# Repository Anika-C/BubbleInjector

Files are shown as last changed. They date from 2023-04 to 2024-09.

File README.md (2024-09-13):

# Bubble Injector

The Bubble Injector is a DIY scientific instrument designed to measure the fracture toughness (K<sub>Ic</sub>) of cohesive sediments using a bubble injection method. The system induces fracture in sediment samples by incrementally injecting air through a needle. The rising air pressure is monitored until it drops abruptly, indicating bubble formation. Fracture toughness is then calculated from the peak pressure at which fracture occurred. The system allows for measuring a depth profile with small-scale resolution and has produced measurements that compare well to past data.

This GitHub repository is meant to accompany the article: 
  Cho, Anika S., Dorgan, Kelly M., Lockridge, Grant. “Small-scale measurement of fracture toughness of muddy marine sediments via bubble injection.” Limnology and       Oceanography: Methods, vol. 22, no. 8, 18 May 2024, pp. 527–535,
  https://doi.org/10.1002/lom3.10625

## Hardware
  + Syringe Pump:
    + NEMA Stepper Motor
    + 3mL Syringe
    + 80/20 Linear Motion Bearing/Frame
    + Custom aluminum parts (CAD files available)
  + Electronics:
    + Arduino Zero + SD Card Shield
    + TinyG CNC Controller (v8)
    + 4-20mA Pressure Sensor (0-15 PSI)
    
Assembly details, full parts list, and cost estimate available in repo.

G-code & Setup Reference: https://github.com/synthetos/TinyG/wiki/Homing-and-Limits-Description-and-Operation

TinyG CNC Stepper Motor Controller configuration details: **TinyG_Config_Settings.txt**

## Code
**Bubble_Injection_Aug2022.ino**: Initiates automatic air injection procedures based on serial input, logs pressure sensor data to an SD card

**processBubble.m**: Plots pressure data, identifies critical peak pressure, and calculates (K<sub>Ic</sub>)

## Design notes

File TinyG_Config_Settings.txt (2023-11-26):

Adjust TinyG settings through the Arduino IDE
Serial input:
"$z" to display all settings for z axis 
"$3" to display all settings for m3 (motor 3, z axis)

Individually view and/or change settings:
Ex: "$3sa = ?" to view current ztm (z travel maximum) setting
Ex: "$3sa = 0.9" to change m3 step angle to 0.9 degrees

Zaxis Settings - 1/4-20 lead screw, 3mL syringe
[zam] z axis mode                 1 [standard]
[zvm] z velocity maximum        800 mm/min
[zfr] z feedrate maximum        800 mm/min
[ztn] z travel minimum         -160.000 mm
[ztm] z travel maximum           75.000 mm
[zjm] z jerk maximum             20 mm/min^3 * 1 million
[zjh] z jerk homing              40 mm/min^3 * 1 million
[zjd] z junction deviation        0.0500 mm 
[zsn] z switch min                0 [0=off,1=homing,2=limit,3=limit+homing]
[zsx] z switch max                3 [0=off,1=homing,2=limit,3=limit+homing]
[zsv] z search velocity          35 mm/min
[zlv] z latch velocity           15 mm/min
[zlb] z latch backoff             0.500 mm
[zzb] z zero backoff              3.300 mm

[3ma] m3 map to axis              2 [0=X,1=Y,2=Z...]
[3sa] m3 step angle               0.900 deg
[3tr] m3 travel per revolution    0.07463 mL		// 1/4-20 lead screw = 1.27mm/rotation
			    	  			// (1.27mm/rev) * (1mL/17.0168mm for 3mL syringe) = 0.07463mL/rev
[3mi] m3 microsteps               8 [1,2,4,8]
[3po] m3 polarity                 0 [0=normal,1=reverse]
[3pm] m3 power management         2 [0=disabled,1=always on,2=in cycle,3=when moving]

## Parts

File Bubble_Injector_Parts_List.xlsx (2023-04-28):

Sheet: Syringe_Pump
Syringe Pump Build Supply List
Item | Size/Specs | Supplier | Supplier PN | Cost Per | Count Total | Total | Link | Notes
Raw Stock
Aluminum T-slot Extrusion | 1 x 1 x 12 inch | 8020 | 1010 | $7.23 | 1 | $7.23 | https://8020.net/1010.html | T-Slotted Framing (#1)
Aluminum Bar | 3 x 5 x 1 inch |  |  |  |  |  |  | Syringe Barrel Holder (#3)
Aluminum Rod | 2.5 dia x 1.5 inch long |  |  |  |  |  |  | 3mL Syringe Adapter (#4)
Aluminum Bar | 3 x 5 x 1 inch |  |  |  |  |  |  | Syringe Plunger Mount (#5)
Aluminum Bar | 3 x 2.5 x 1 inch |  |  |  |  |  |  | Syringe Depressor Clamp (#6)
Aluminum Bar | 3 x 3 x 1 inch |  |  |  |  |  |  | Syringe Bearing End (#10)
Aluminum Bar | 0.5 x 0.5 x 10 inch |  |  |  |  |  |  | Cross Support (#12)
Parts
Single Mount Unibearing | 10 Series Short | 8020 | 6730 | $50.91 | 1 | $50.91 | https://8020.net/6730.html | Linear Bearing 8020 (#2)
3mL Syringe | Luer Lock Connection | McMaster | 7510A651 | $7.62 | 1 | $7.62 | https://www.mcmaster.com/7510A651/ | Pack of 10
Limit Switches |  | Amazon |  | $5.98 | 1 | $5.98 | https://www.amazon.com/HiLetgo-KW12-3-Roller-Switch-Normally/dp/B07X142VGC | Pack of 100
Shaft Coupling 1/4 inch to 5mm | 1/4 inch to 5mm | Amazon |  | $10.69 | 1 | $10.69 | https://www.amazon.com/Xnrtop-Coupling-Diameter-Aluminum-Connector/dp/B07YFMF2Z6 | Pack of 2
Stepper Motor | NEMA 17 | Amazon |  | $13.95 | 1 | $13.95 | https://www.amazon.com/STEPPERONLINE-Stepper-Bipolar-Connector-compatible/dp/B00PNEQKC0
Ball Bearing | R4 | McMaster Carr | 57155K305 | $6.42 | 2 | $12.84 | https://www.mcmaster.com/57155K305/
Hardware
6-32 x Socket Head Screw | 1/2 inch long, Stainless | McMaster Carr | 92196A148 | $8.72 | 1 | $8.72 | https://www.mcmaster.com/92196A148/ | Pack of 100
4-40 Socket Head Screw | 3/8 inch long, Stainless | McMaster Carr | 92196A108 | $6.30 | 1 | $6.30 | https://www.mcmaster.com/92196A108/ | Pack of 100
10-32 Socket Head Screw | 3/4 inch long, Stainless | McMaster Carr | 92196A272 | $19.56 | 1 | $19.56 | https://www.mcmaster.com/92196A272/ | Pack of 100
10-32 Socket Head Screw | 1/2 inch long, Stainless | McMaster Carr | 92196A269 | $15.47 | 1 | $15.47 | https://www.mcmaster.com/92196A269/ | Pack of 100
10-32 T Nut | Stainless | McMaster Carr | 94581A128 | $14.32 | 1 | $14.32 | https://www.mcmaster.com/94581A128/ | Pack of 10
1/4-20 Socket Head Screw | 3/4 inch long, Stainless | McMaster Carr | 92196A540 | $23.83 | 1 | $23.83 | https://www.mcmaster.com/92196A540/ | Pack of 50
1/4-20 Socket Head Screw | 3 inch long, Stainless | McMaster Carr | 92196A553 | $15.31 | 1 | $15.31 | https://www.mcmaster.com/92196A553/ | Pack of 10
1/4-20 Threaded Rod | 1 ft long, Stainless | McMaster Carr | 98804A487 | $2.31 | 1 | $2.31 | https://www.mcmaster.com/98804A487/
1/4-20 Nut |  | McMaster Carr | 92673A113 | $3.55 | 1 | $3.55 | https://www.mcmaster.com/92673A113/ | Pack of 50
M3 x 0.35 Socket Head Screw | 16 mm long, Stainless | McMaster Carr | 90751A114 | $15.73 | 1 | $15.73 | https://www.mcmaster.com/90751A114/ | Pack of 100
 |  |  |  |  | TOTAL | $234.32

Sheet: Electonics_Controller
Electronics Control Box Supply List
Item | Size/Specs | Supplier | Supplier PN | Cost per | Count total | Total | Link | Notes
Boards/Sensors
Arduino Zero |  | Amazon | ABX00003 | $49.50 | 1 | $49.50 | https://www.amazon.com/Arduino-Zero-ABX00003/dp/B09CMCXVV4
SD Card Shield |  | Adafruit | 1141 | $13.95 | 1 | $13.95 | https://www.adafruit.com/product/1141
Screw Shield R3 |  | Adafruit | 196 | $14.95 | 1 | $14.95 | https://www.adafruit.com/product/196
TinyG Controller v8 |  | Adafruit | 1749 | $165.00 | 1 | $165.00 | https://www.adafruit.com/product/1749
Voltage Adapter | AC110 to 24VDC 4A | Amazon |  | $8.46 | 1 | $8.46 | https://www.amazon.com/Switch-Supply-Module-Isolated-Output/dp/B07GWCPTQB
Pressure Sensor | 4-20mA, 0-15psig | Omega | PX309-015GI | $331.43 | 1 | $331.43 | https://www.omega.com/en-us/pressure-measurement/pressure-transducers/px309/p/PX309-015GI
Components/Hardware
Screw Terminal | 5mm pitch, 2 pos | Mouser | 490-TB002-500-02BE | $0.65 | 1 | $0.65 | https://www.mouser.com/ProductDetail/CUI-Devices/TB002-500-02BE?qs=vLWxofP3U2x9716kcgva%2Fw%3D%3D
Terminal Block | 20A, 300VAC, 4 pos | McMaster Carr | 7527K44 | $2.54 | 1 | $2.54 | https://www.mcmaster.com/7527K44/
Fuse Holder | 6 x 32mm fuse | Mouser | 504-BK2-S-4202-1X-R | $1.95 | 1 | $1.95 | https://www.mouser.com/ProductDetail/Bussmann-Eaton/BK2-S-4202-1X-R?qs=DRkmTr78QASifKBhsRdWiQ%3D%3D
Din 5 pin bulkhead |  | Amazon |  | $6.99 | 1 | $6.99 | https://www.amazon.com/CESS-Female-Socket-Connector-Soldering/dp/B01GBT9RC0 | Pack of 4
USB Bulkhead |  | Amazon |  | $13.89 | 1 | $13.89 | https://www.amazon.com/Anmbest-Electrical-Waterproof-Connector-Industrial/dp/B07RPW5XGB/ | Pack of 2
AC Power Socket Male | 10A, 250V | Amazon |  | $7.99 | 1 | $7.99 | https://www.amazon.com/button-Adapter-Connector-Socket-MXRS/dp/B082ZFRV1B | Pack of 3
Circuit Components
Resistor | 390 ohm, 1/4 watt | Mouser | 708-RNMF14FAD390R | $0.01 | 1 | $0.01 | https://www.mouser.com/ProductDetail/SEI-Stackpole/RNMF14FAD390R
Tantalum Capacitor | 1 uF | Mouser | 581-TAP105M050CRW | $0.85 | 1 | $0.85 | https://www.mouser.com/ProductDetail/AVX/TAP105M050CRW/?qs=D60Q9NgkslkPfEe0TVgP8Q%3D%3D
Tantalum Capacitor | 0.1 uF | Mouser | 80-T356A104K35AT | $1.31 | 1 | $1.31 | https://www.mouser.com/ProductDetail/KEMET/T356A104K035AT
Zener Diode | 3.6v, 5.1watt | Amazon |  | $4.99 | 1 | $4.99 | https://www.amazon.com/1N4733A-1N4733-Silicon-Planar-DO-204AL/dp/B07WK46MK4?th=1 | Pack of 20
 |  |  |  |  | TOTAL | $624.46

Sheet: Assembly
Bubble Injector Assembly Supply List
Item | Size/Specs | Supplier | Supplier PN | Cost per | Count total | Total | Link | Notes
Air Injection System
14G Dispensing Needle | 2 inch long, Point Style 5 (Non-Coring), Luer Lock | Hamilton | 7746-15 | $133.00 | 1 | $133.00 | https://www.hamiltoncompany.com/laboratory-products/needles/7746-15 | Pack of 6
22G Dispensing Needle | 2 inch long, Point Style 5 (Non-Coring), Luer Lock | Hamilton | 7746-06 | $133.00 | 1 | $133.00 | https://www.hamiltoncompany.com/laboratory-products/needles/7746-06 | Pack of 6
1/4" Tubing | Clear, 5/32" ID | McMaster | 5648K69 | $0.65 | 2 | $1.30 | https://www.mcmaster.com/5648K69-5648K256/ | Per Foot
Stop Valve | Male x Female, Luer Lock | McMaster | 7033T24 | $2.66 | 1 | $2.66 | https://www.mcmaster.com/7033T24/
Threaded Tube Coupling | 10-32 x Male Adapter, Luer Lock | McMaster | 51525K428 | $6.72 | 1 | $6.72 | https://www.mcmaster.com/51525K428/ | Pack of 10
Female Tube Coupling | 5/32" Tube ID x Female Luer Lock | McMaster | 51525K214 | $5.09 | 1 | $5.09 | https://www.mcmaster.com/51525K214/ | Pack of 10
Male Tube Coupling | 5/32" Tube ID x Male Luer Lock | McMaster | 51525K124 | $6.26 | 1 | $6.26 | https://www.mcmaster.com/51525K124/ | Pack of 10
Assembly & Testing Materials
Multi-Axis Manual Micromanipulator | 3mm - 12.7mm Tool Clamp |  |  |  |  |  | https://www.wpi-europe.com/products/micromanipulators/manual-manipulators/m325.aspx | Used part unavailable, substitute part linked
10mm Steel Rod | 1-1/2 feet long | McMaster | 1272T41 | $26.92 | 1 | $26.92 | https://www.mcmaster.com/1272T41-1272T412/ | Micromanipulator mount
Aluminum Tubing | 1/4" OD, 0.02" Wall Thickness | McMaster | 89965K341 | $7.16 | 1 | $7.16 | https://www.mcmaster.com/89965K341/ | Per Foot
1/4" Acrylic Stock | 12 x 12 x 0.25 inch, Clear | McMaster | 8560K354 | $18.38 | 2 | $36.76 | https://www.mcmaster.com/8560K354/ | Platform
1/4" Aluminum Unthreaded Spacer | 1/4" Screw Size, 1-1/2 inch long | McMaster | 92510A771 | $4.25 | 4 | $17.00 | https://www.mcmaster.com/92510A771/ | Platform Spacers
1/4-20 Hex Head Screw | 2-1/2 inch long | McMaster | 92240A552 | $7.74 | 1 | $7.74 | https://www.mcmaster.com/92240A552/ | Pack of 25
6" Plastic Dish | 0.75 inch depth, Clear | Amazon |  | $9.39 | 1 | $9.39 | https://www.amazon.com/Plastic-Petri-Dish-Lid-Polypropylene/dp/B08X4VD3XY
4" (10cm) Acrylic Tube | 12 inch long, Clear | Amazon |  | $7.86 | 1 | $7.86 | https://www.amazon.com/FixtureDisplays-Acrylic-Diameter-15139-12-1PK-NF/dp/B086KT4F8N | Testing Core
 |  |  |  |  | TOTAL | $400.86

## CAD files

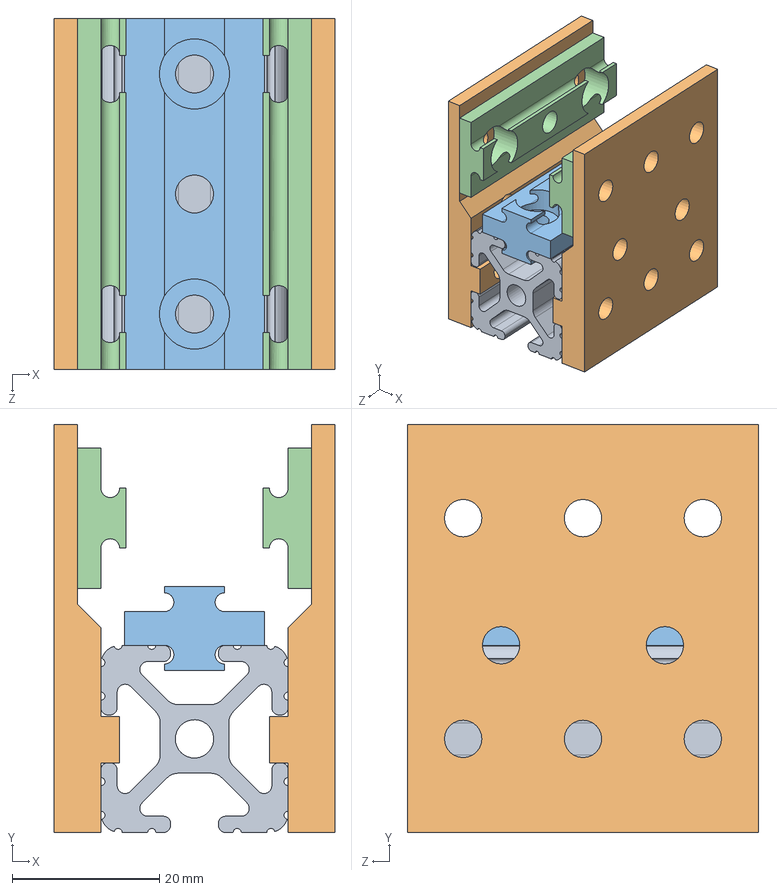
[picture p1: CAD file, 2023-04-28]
Syringe Pump CAD Model/LinearBearing_8020_pn6730.SLDASM
38.1 x 55.3 x 47.6 mm
T-Slotted Framing_1.875
BearingSide x 2
Pad_Bearing_Upper
Pad_Bearing x 2

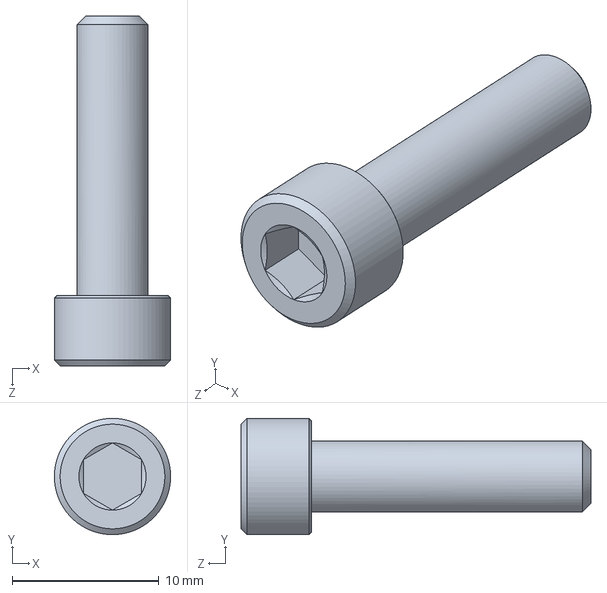
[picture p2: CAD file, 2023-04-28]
Syringe Pump CAD Model/Hardware/10-32_x0.75_ SocketHead.SLDPRT
7.94 x 7.94 x 23.9 mm

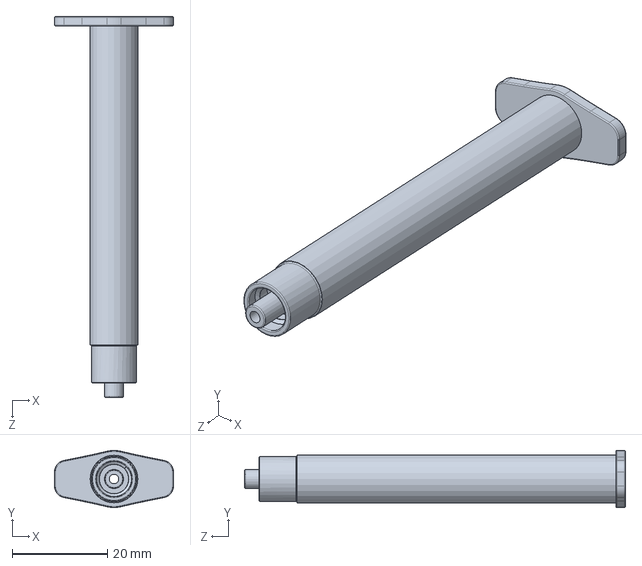
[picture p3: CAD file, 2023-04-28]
Syringe Pump CAD Model/Hardware/syringe 3ml part 01.SLDPRT
25.0 x 12.0 x 80.0 mm

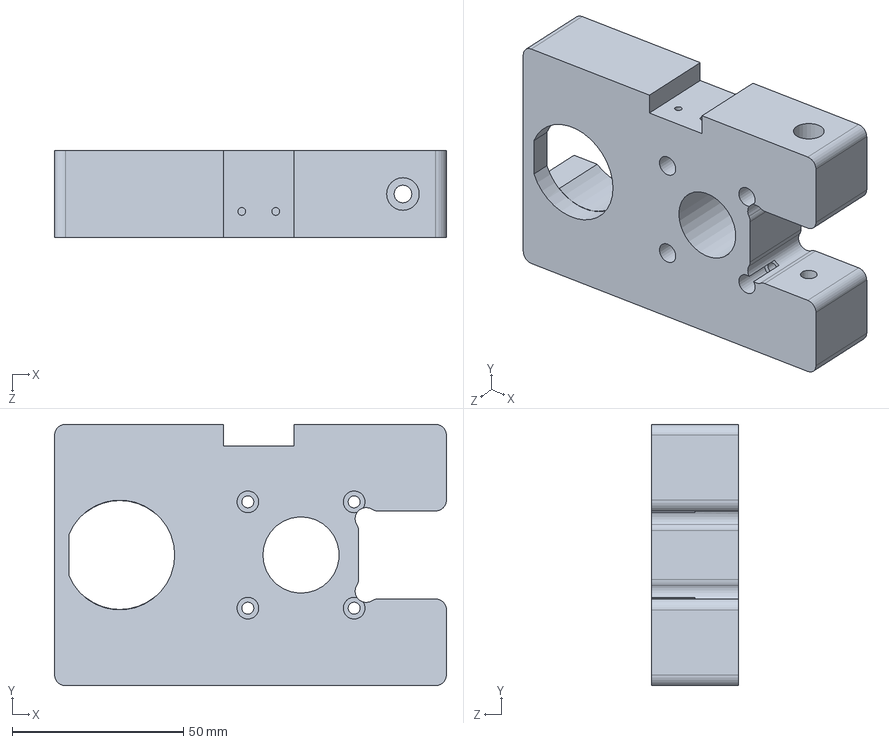
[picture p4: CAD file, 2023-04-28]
Syringe Pump CAD Model/Syringe_Plunger_Mount_v1.SLDPRT
114.3 x 76.2 x 25.4 mm

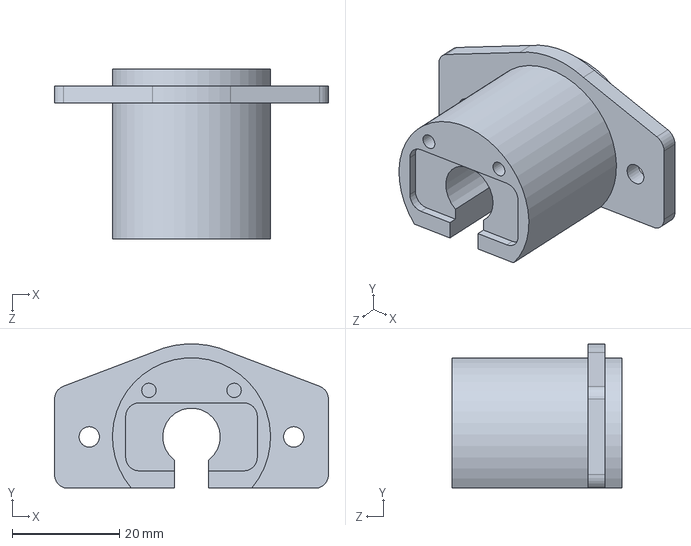
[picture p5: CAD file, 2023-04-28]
Syringe Pump CAD Model/3mL_Adapter_v1.SLDPRT
51.1 x 26.8 x 31.8 mm

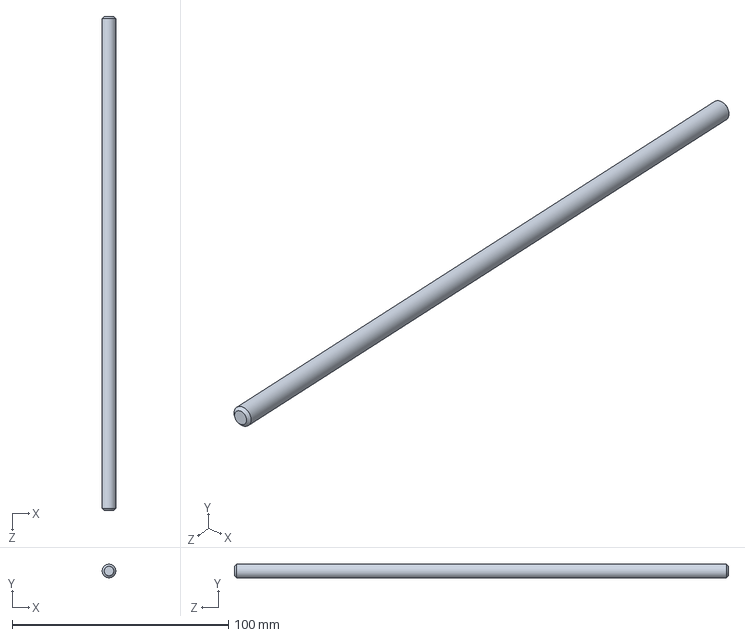
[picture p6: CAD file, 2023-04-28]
Syringe Pump CAD Model/Hardware/1_4-20_Threaded Rod_10in.SLDPRT
6.35 x 6.35 x 228.6 mm

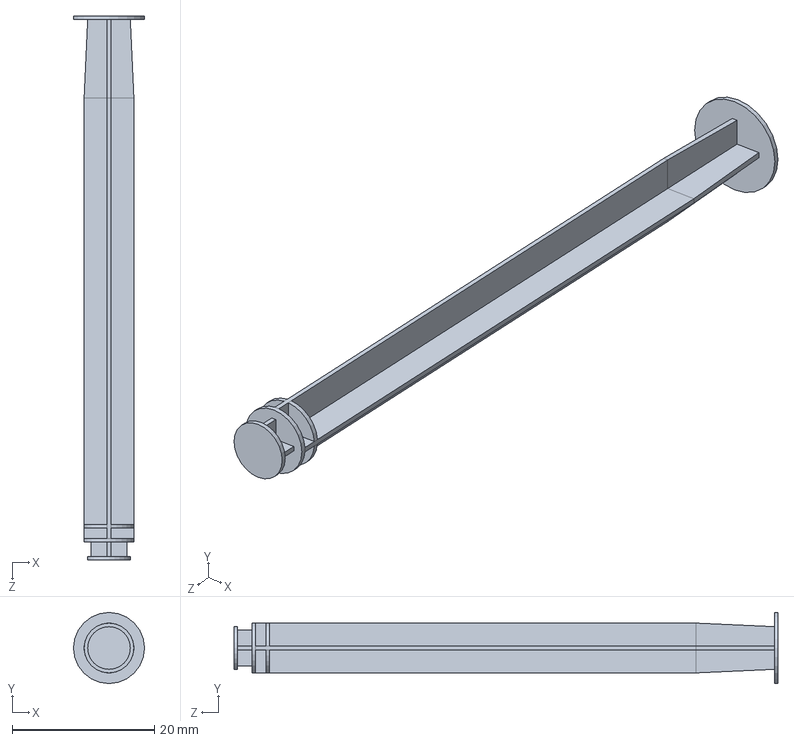
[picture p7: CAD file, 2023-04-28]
Syringe Pump CAD Model/Hardware/syringe 3ml part 02.SLDPRT
10.0 x 10.0 x 76.5 mm

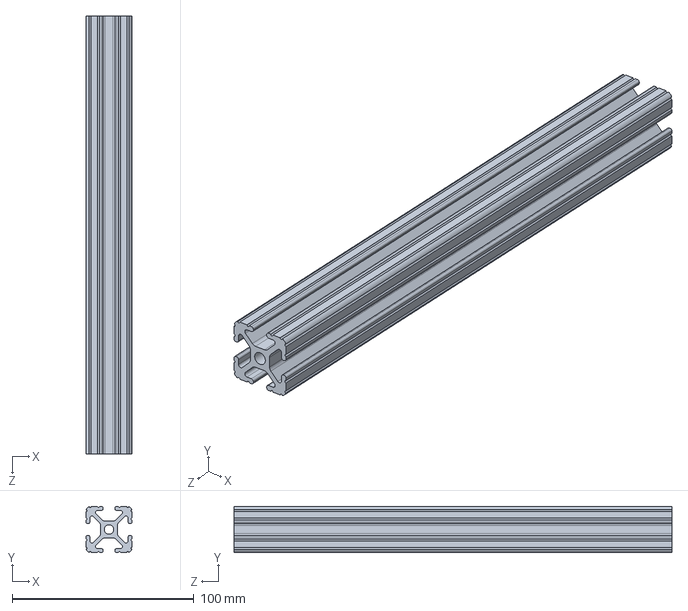
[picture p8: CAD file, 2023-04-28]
Syringe Pump CAD Model/T-Slotted Framing12.SLDPRT
25.4 x 25.4 x 241.3 mm

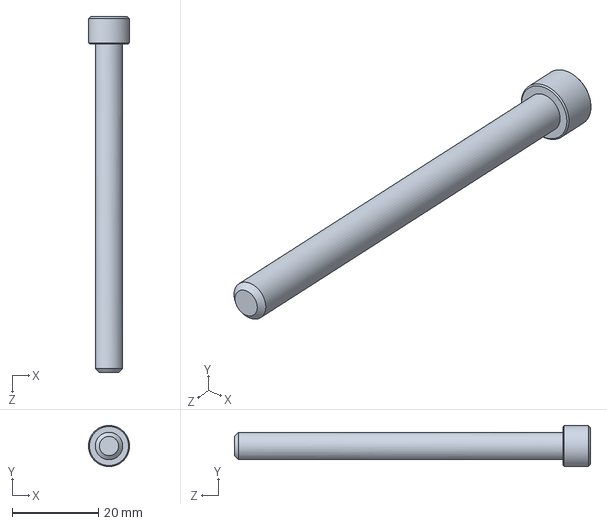
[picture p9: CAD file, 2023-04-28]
Syringe Pump CAD Model/Hardware/1_4-20_x3_ SocketHead.SLDPRT
9.53 x 9.52 x 82.5 mm

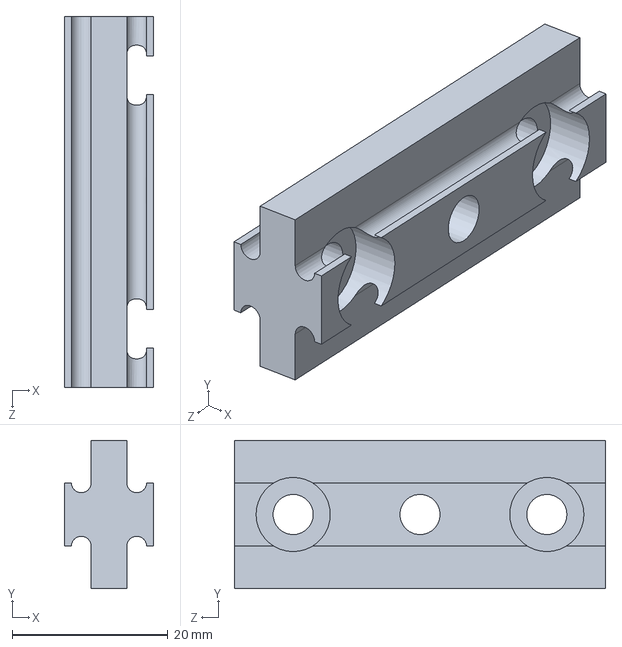
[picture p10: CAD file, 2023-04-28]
Syringe Pump CAD Model/Pad_Bearing_Upper.SLDPRT
11.4 x 19.1 x 47.6 mm

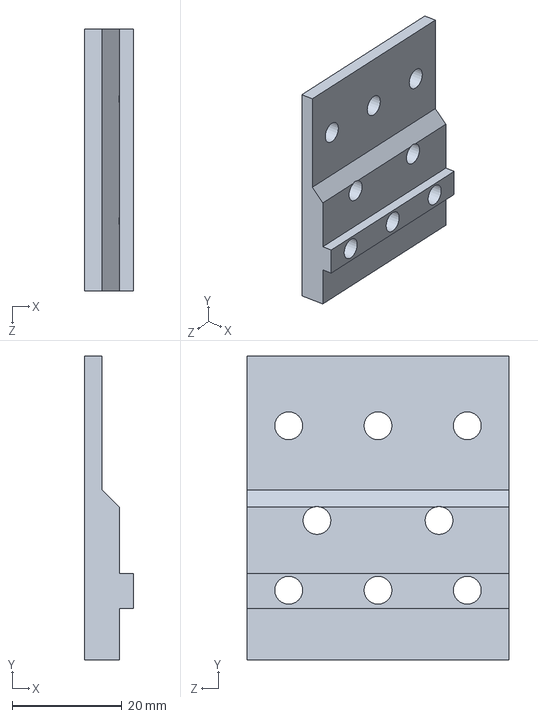
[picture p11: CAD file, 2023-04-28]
Syringe Pump CAD Model/BearingSide.SLDPRT
8.89 x 55.3 x 47.6 mm

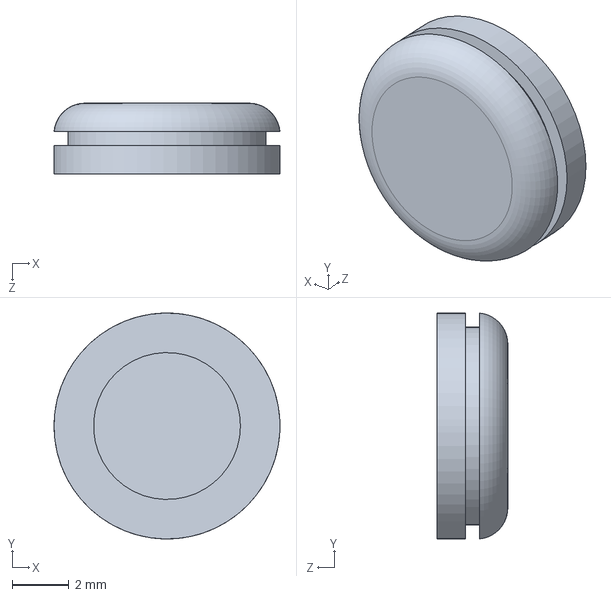
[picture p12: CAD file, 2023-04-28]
Syringe Pump CAD Model/Hardware/syringe 3ml part 03.SLDPRT
7.99 x 7.99 x 2.50 mm

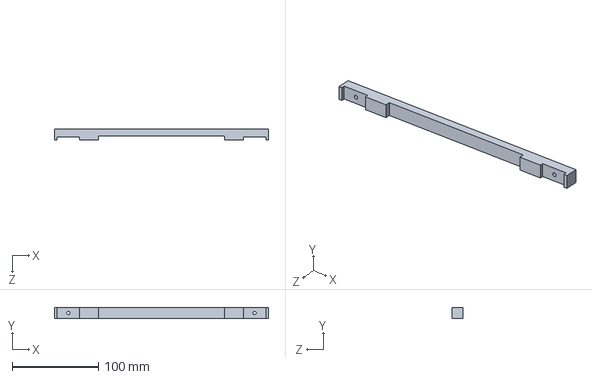
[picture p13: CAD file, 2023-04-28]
Syringe Pump CAD Model/CrossSupport_v1.SLDPRT
247.9 x 12.7 x 12.7 mm

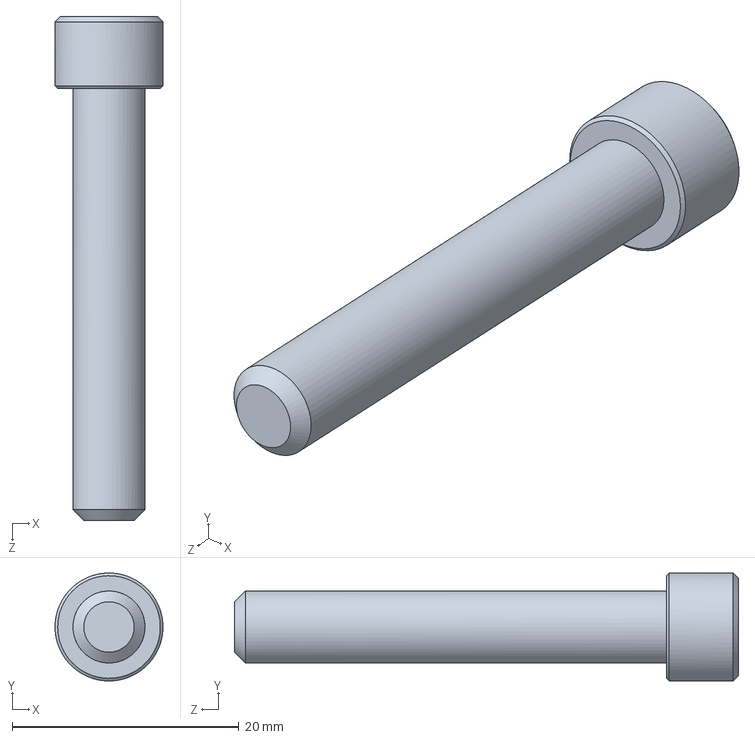
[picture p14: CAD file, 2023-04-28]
Syringe Pump CAD Model/Hardware/1_4-20_x1.5_ SocketHead.SLDPRT
9.53 x 9.52 x 44.5 mm

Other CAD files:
Syringe Pump CAD Model/Hardware/limit switch.SLDPRT
Syringe Pump CAD Model/Omega Pressure Transducer.SLDPRT
Syringe Pump CAD Model/Syringe_Depres_Clamp_V1.1.SLDPRT
Syringe Pump CAD Model/SyringeBarrelHolder_v1.SLDPRT
Syringe Pump CAD Model/Hardware/10-32_T_Nut.SLDPRT
Syringe Pump CAD Model/Hardware/10-32_x0.5_ SocketHead.SLDPRT
Syringe Pump CAD Model/Hardware/1_4-20_x0.75_ SocketHead.SLDPRT
Syringe Pump CAD Model/Hardware/4-40_x0.375_ SocketHead.SLDPRT
Syringe Pump CAD Model/Hardware/6_32_x0.5_SocketHead.SLDPRT
Syringe Pump CAD Model/Hardware/M3_16mm_SocketHead.SLDPRT
Syringe Pump CAD Model/Hardware/NEMA17_Stepper Motor.SLDPRT
Syringe Pump CAD Model/Hardware/R4_BallBearing.SLDPRT
Syringe Pump CAD Model/Hardware/Shaft Coupling 5mm to 1_4.SLDPRT
Syringe Pump CAD Model/Hardware/T_Nut_Assembly.SLDASM
Syringe Pump CAD Model/Hardware/T_Nut_Assembly_0.75.SLDASM
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

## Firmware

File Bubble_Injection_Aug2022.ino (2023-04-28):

/*
 * Anika Cho
 * Dorgan Lab, Summer 2022
 * Bubble Injection Procedure Code
 * Updated August 2022
 * 
 * Setup: 
 * Mud sample should be extruded into a pre-drilled test core with all bubble injection holes thoroughly taped closed
 * Check connections: USB power from computer to Arduino Zero, standard wall outlet to power supply/electronics box, stepper motor cable to "Z axis" port, pressure sensor & Z-limit switch to labelled USB ports
 * Place the test core in the tray and slide into the circular slot on the test platform
 * Upload this Bubble Injection program to the Arduino Zero
 * 
 * Bubble Injection Testing Procedure:
 * 1) Reset the syringe by entering the command "r" to the serial monitor/plotter
 * 2) Check the needle for clogs by flushing the needle with warm water and air using a hand-held syringe
 *    Use 14G non-coring needle for mud, 22G non-coring needle for jello
 * 3) Firmly screw the needle into the stop valve with the needle port oriented sideways, then use the micromanipulator to align the needle with an injection hole
 * 4) Use the micromanipulator to fully insert the needle into the sediment core through the tape
 * 4) Verify that the SD Card is in the SD Card Shield and hit the Reset button on the Arduino Zero to begin logging pressure data to a new file
 * 5) Input the chosen procedure command to the serial monitor/plotter to begin the air injection cycle
 *    ("j" for jello, "m" for mud)
 * 6) Monitor the live pressure plot generated by the serial plotter until a clear pressure drop is observed (bubble formation)
 *    Orange line = Pressure (PSI), Grey line = Analog Voltage Input
 * 7) Hit the Reset button on the TinyG board to stop air injection after bubble formation
 * 8) Remove the SD card to stop logging pressure data and save the file
 * 9) Fully retract the needle from the core and tape over the puncture hole to prevent water leakage
 */

//*********************************** INITIAL SETUP ***********************************************

#include <Wire.h>
#include <Adafruit_ADS1X15.h>
#include <SPI.h>
#include <SD.h>

// Number of milliseconds between grabbing and logging data. 1000 ms = once a second
#define LOG_INTERVAL  10    // ms between entries (reduce to take more/faster data)

// Number of milliseconds before writing the logged data permanently to disk
// Set to the LOG_INTERVAL to write each time (safest)
// Set to 10*LOG_INTERVAL to write all data every 10 datareads
// Could lose the last 10 datareads if power is lost, but consumes less power & is much faster!
#define SYNC_INTERVAL 100 // mills between calls to flush() - to write data to the card

uint32_t syncTime = 0;      // time of last sync()

#define ECHO_TO_SERIAL   1  // echo data to serial port
#define WAIT_TO_START    0  // Wait for serial input in setup()

// For the data logging shield, we use digital pin 10 for the SD cs line
const int chipSelect = 10;  //THIS NEEDS TO BE JUMPED FROM THE NORMAL PIN 10 ON THE SD CARD SHIELD

// Data logging file
File logfile;


//*********************************** TEST ARDUINO COMMS ***********************************************

int val = 0;
void error(char *str)
{
  SerialUSB.print("error: ");
  SerialUSB.println(str);
  while (1);
}

//*********************************** CAPTURE SERIAL DATA FROM TINYG ***********************************************

const byte numChars = 43;
char receivedChars[numChars];
char tempChars[numChars];        // temporary array for use when parsing

// variables to hold the parsed data
char messageFromPC[numChars] = {0};
int integerFromPC = 0;
float floatFromPC = 0.0;
float Zpos = 0.000;
float Apos = 0.000;
boolean newData = false;

//*********************************** PRESSURE SENSOR SETUP ***********************************************

const int pressureSensorIn = A1;  // analog input pin that the pressure sensor is attached to
int sensorValue = 0;              // value read from the pressure sensor
float PSI = 0;                    // value output to the PWM (analog out)
float sensorVolt = 0;             // voltage from the pressure sensor
  
Adafruit_ADS1015 ads;     /* Use this for the 12-bit version */


//*********************************** BUTTONS ***********************************************

const int buttonD8 = 8 ; // button with pin
int buttonStateD8 = 0 ;

const int buttonD5 = 5 ; // button with pin
int buttonStateD5 = 0 ;

const int buttonD6 = 6 ; // button with pin
int buttonStateD6 = 0 ;

const int buttonD7 = 7 ; // button with pin
int buttonStateD7 = 0 ;


//*********************************** SETUP SERIAL COMMS & SD CARD LOG FILE ***********************************************

void setup()
{
  SerialUSB.begin (115200);
  Serial1.begin (115200);
  Serial.begin (115200);

  pinMode(buttonD8, INPUT);
  pinMode(buttonD5, INPUT);
  pinMode(buttonD6, INPUT);
  pinMode(buttonD7, INPUT);

  delay (500); // setting TinyG position output

  Serial1.println("?");
  Serial1.println("{\"sr\":{\"posx\":t, \"posy\":t,\"posz\":t,\"posa\":t}}");
  Serial1.println("$qv=0");  // setting the Queue Report Verbosity to zero (disable) to prevent qr:xx from appearing in the serial feed
  Serial1.println("$sv=2");  // setting the status report to "verbose" so all positions show all the time


  Serial1.println("?");

  // Initialize the SD card
  SerialUSB.print("Initializing SD card...");
  pinMode(10, OUTPUT); 

  // Verify that the card is present and can be initialized
  if (!SD.begin(chipSelect)) {
    error("Card failed, or not present");
  }
  Serial.println("card initialized.");

  // Create a new file
  char filename[] = "BUBBLE00.CSV";
  for (uint8_t i = 0; i < 100; i++) {
    filename[6] = i / 10 + '0';
    filename[7] = i % 10 + '0';
    if (! SD.exists(filename)){   // only open a new file if it doesn't exist
      logfile = SD.open(filename, FILE_WRITE);
      break;
    }
  }

  if (!logfile) {
    error("couldnt create file");
  }

  SerialUSB.print("Logging to: ");
  SerialUSB.println(filename);
  
  logfile.println("Millis,Pressure,RawPressure,Z");  // CHANGE THESE HEADERS TO WHATEVER YOU WANT
  delay (50);
}


//*********************************** MAIN LOOP ***********************************************

void loop () {
  
  analogReadResolution(12);                     // changing the resolution (from 8bit to 12bit) of the analong read

  sensorValue = analogRead(pressureSensorIn);   // collect data from pressure sensor analog input A1
  sensorVolt = sensorValue * (3.3/4095.0);      // map sensor value to the range of analog out: 3.3V input voltage max / 2^12 bit resolution

  PSI = (sensorVolt * 3.6138) - 3.8668;         // calibrated conversion equation for half range Omega 15PSI, 4-20mA (CHANGE BASED ON SENSOR CALIBRATION)
  
  uint32_t m = millis();

  while (Serial1.available() > 0) {
    recvWithStartEndMarkers();
    if (newData == true) {
      strcpy(tempChars, receivedChars);
      // this temporary copy is necessary to protect the original data
      // because strtok() used in parseData() replaces the commas with \0
      parseData();
      // showParsedData();
      newData = false;
    }
  }

  // read from port 0, send to port 1:
  while (SerialUSB.available() > 0) {
    char inByte = SerialUSB.read();


//*********************************** BUBBLE INJECTION PROCEDURE CASES ***********************************************

  //Type case letter in serial monitor input to initiate procedure
  
    switch (inByte) {

      case 'r': // RESET SYRINGE PUMP, ZERO THE Z-AXIS
        Serial1.print("g28.2 z0"); // gcode command
        Serial1.print('\r');
        ;
        break;  // end reset procedure
        
      case 'j': // JELLO PROCEDURE
      // Inject 0.05 mL at a time, speed f1, wait 5 seconds between runs
        Serial1.print("g1z0.05f1"); //Inject 0.05mL initially
        Serial1.print('\r');
        Serial1.print("g4p5"); // pause 5 seconds
        Serial1.print('\r');
        Serial1.print("g91"); //Enter incremental motion mode
        Serial1.print('\r');

        for (int i = 1; i < 90; i++) {
          Serial1.print("g1z0.05"); // increment z axis position up by 0.05mL
          Serial1.print('\r');
          Serial1.print("g4p5"); // pause 5 seconds
          Serial1.print('\r');
        }
        break; // end jello procedure


      case 'm': // MUD PROCEDURE
        // Inject 0.1 mL at a time, speed f2, wait 5 seconds between runs
        Serial1.print("g1z0.1f2"); //Inject 0.1mL initially
        Serial1.print('\r');
        Serial1.print("g4p5"); // pause 5 seconds
        Serial1.print('\r');
        Serial1.print("g91"); //Enter incremental motion mode
        Serial1.print('\r');

        for (int i = 1; i < 30; i++) {
          Serial1.print("g1z0.1"); // increment z axis position up by 0.1mL
          Serial1.print('\r');
          Serial1.print("g4p5"); // pause 5 seconds
          Serial1.print('\r');
        }
        break; // end mud procedure

    }
    Serial1.write(inByte);
  }


//*********************************** PRINT/VIEW SERIAL DATA ***********************************************

// Print data to SD Card
  logfile.print(m); //milliseconds since start
  logfile.print(",");
  logfile.print(PSI, 4);  //print PSI to 4 decimal places; column2
  logfile.print(",");
  logfile.print(sensorValue); //column3
  logfile.print(",");
  logfile.print(Zpos, 4); // column4
  logfile.println(",");

// Print data to Serial Monitor/Plotter
// Note: Some values omitted to simplify live plot display (UNCOMMENT TO DISPLAY MORE SERIAL DATA)
if (m % 100 == 0){
  #if ECHO_TO_SERIAL
    SerialUSB.print("Min:-0.5, Max:3.3");
    SerialUSB.print(",   ");
    //SerialUSB.print(m);         // milliseconds since start
    //SerialUSB.print(",   ");
    SerialUSB.print("PSI: ");
    SerialUSB.print (PSI, 4);     // print PSI to 4 decimal places
    SerialUSB.print(",   ");
    //SerialUSB.print(sensorValue);
    //SerialUSB.print(",   ");
    SerialUSB.print("sensorVolt: ");
    SerialUSB.print(sensorVolt);
    //SerialUSB.print(",   ");
    //SerialUSB.print(Zpos, 4);
    SerialUSB.println(",");
  #endif
}

  if ((millis() - syncTime) < SYNC_INTERVAL) return;
  syncTime = millis();
  logfile.flush();

}

//*********************************** END MAIN LOOP ***********************************************


void recvWithStartEndMarkers() {
  static boolean recvInProgress = false;
  static byte ndx = 0;
  char startMarker = ':';
  char endMarker = '\n';
  char rc;

  rc = Serial1.read();

  if (recvInProgress == true) {
    if (rc != endMarker) {
      receivedChars[ndx] = rc;
      ndx++;
      if (ndx >= numChars) {
        ndx = numChars - 1;
      }
    }
    else {
      receivedChars[ndx] = '\0'; // terminate the string
      recvInProgress = false;
      ndx = 0;
      newData = true;
    }
  }

  else if (rc == startMarker) {
    recvInProgress = true;
  }
}

void parseData() {      // split the data into its parts
  char * strtokIndx; // this is used by strtok() as an index
  strtokIndx = strtok(NULL, ":");
  Zpos = atof(strtokIndx);     // convert this part to a float
  strtokIndx = strtok(NULL, ":");
  Apos = atof(strtokIndx);     // convert this part to a float
}

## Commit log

2023-04-28 Add files via upload
    Parts list & cost estimate for syringe pump, electronics control box, overall assembly
    [BubbleInjectorPartsList.xlsx]
2023-04-28 Arduino code for bubble injection procedure
2023-04-28 Parts list & cost estimate
    [Bubble_Injector_Parts_List.xlsx]
2023-04-28 Syringe pump CAD files (Solidworks)
    [10-32_T_Nut.SLDPRT, 10-32_x0.5_ SocketHead.SLDPRT, 10-32_x0.75_ SocketHead.SLDPRT, 1_4-20_Threaded Rod_10in.SLDPRT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]
